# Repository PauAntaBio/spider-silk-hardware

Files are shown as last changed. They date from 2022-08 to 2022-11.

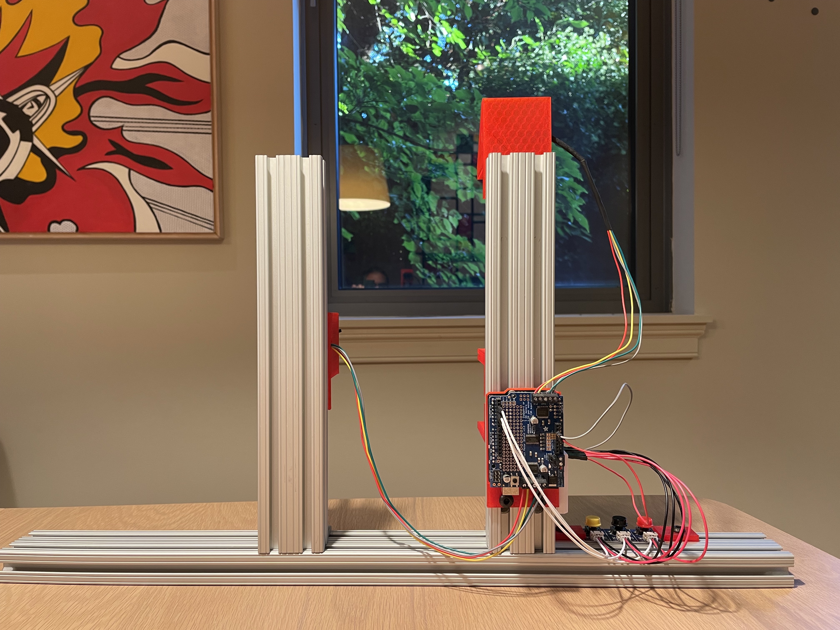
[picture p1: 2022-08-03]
pictures/3 back.jpg

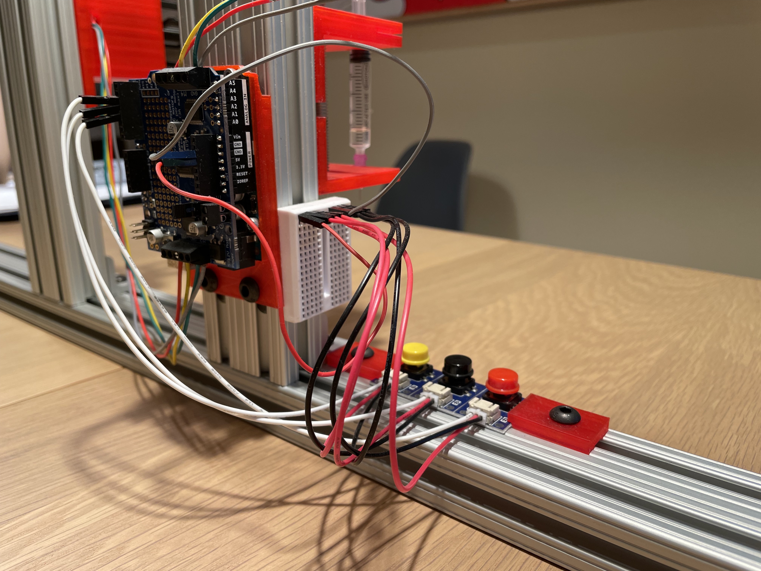
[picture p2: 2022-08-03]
pictures/4 details.jpg

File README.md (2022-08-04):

# spider-silk-hardware

There are many techniques to spin spider silk, the easiest of which is wet spinning, in which the spidroins are dissolved in a chemical solution (for example, saturated ammonium, hexafluoroisopropanol in methanol, hexafluoroacetone hydrate in methanol, and formic acid in methanol) before entering a coagulation bath that removes the solvent and causes conformational changes [1, 2]. To do wet spinning, we need a microsyringe pump capable of extruding the dope at a flowrate as slow as 1 μL/min into a coagulation bath. Once the spidroins have coagulated, a post-spinning roller will collect the spider silk. Because of the microsyringe pump’s design, shear force will help in the coagulation process of the spidroins [1, 2, 3]. Moreover, once the spidroins and gold nanoparticles are in the syringe the oxygen will be purged with Nitrogen gas to increase the chances of binding the gold nanoparticles and spidroins together.



Figure. A) Microsyringe Pump based on a micro-controller-enabled stepper motor that pushes the syringe at the desired flowrate; B) Coagulation bath where the spidroins will be pushed into. This will be filled with a chemical such as isopropanol; and C) Post-spinning roller that will collect spider silk after it has coagulated.

References

1. Rising, A., Johansson, J. Toward spinning artificial spider silk. Nat Chem Biol 11, 309–315 (2015). https://doi.org/10.1038/nchembio.1789.
2. Madurga, R., Gañán-Calvo, A. M., Plaza, G. R., Guinea, G. V., Elices, M., & Pérez-Rigueiro, J. (2017). Production of High-Performance Bioinspired Silk Fibers by Straining Flow Spinning. Biomacromolecules, 18(4), 1127-1133. https://doi.org/10.1021/acs.biomac.6b01757.
3. Andersson, M., Jia, Q., Abella, A., Lee, X.-Y., Landreh, M., Purhonen, P., Hebert, H., Tenje, M., Robinson, C. V., Meng, Q., Plaza, G. R., Johansson, J., & Rising, A. (2017). Biomimetic spinning of artificial spider silk from a chimeric minispidroin. Nature Chemical Biology, 13(3), 262-264. https://doi.org/10.1038/nchembio.2269.

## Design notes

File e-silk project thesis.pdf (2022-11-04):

# E-Silk: Electrically Conductive Spider Silk

Pau Anta-Clusella, pauanta@icloud.com
https://www.pauanta.bio/e-silk
https://github.com/PauAntaBio/spider-silk-hardware Washington DC.
Draft: August 2022

## Introduction

Spider silk is a biomaterial with excellent physical properties such as high tensile strength, high stretchiness, and high toughness [1, 5, 7]. Because of the fierce nature of spiders, the current method of spider silk production involves producing recombinant spidroins in bacterial systems and spinning them into silk [2, 3, 8]. However, the use of denaturation during the purification and fiber formation of the spidroins leads to spider silk with dissatisfying mechanical properties [5].

Presented within is a novel application for synthetic spider silk: spider silk with electrical conductivity, which could be used in clothing to create circuits or expand the current applications of smart fabrics. Some examples include: stretch sensors, functional buttons, and circuitry that can activate a small device.

By taking advantage of genetic engineering techniques a recombinant spider silk protein was created and expressed in E. coli. This spidroin consists of a N-terminus from major ampullate (MaSP) silk with a repetitive region and C-terminus from minor ampullate silk (MiSP). Further, by adding a tetracysteine motif the spidroin should gain the ability to bind to gold (Au) nanoparticles via disulfide bonds [4]. Gold was chosen for its resistance to oxidation and electrical conductivity.

## Design of Custom Protein

Spidroins vary in length and size but generally consist of three parts: a non-repetitive globular N terminus (NT), an extensive glycine- and alanine-rich repetitive region, and a nonrepetitive globular C terminus (CT) [3]. The NT subunits are bundles of 5 alpha helices; at pH levels above 7 they are monomeric, but dimerizes at pH levels below 6. The dimerization process consists of the alpha helices shifting to form a flat dimer interface, allowing the antiparallel subunits to combine [5]. The CT is a stable and soluble homodimer at pH levels greater than 6.5, but as the pH decreases to below 5.5 it destabilizes and loses its helical structure, instead forming β-sheet fibrils. Increased pCO2 (partial pressure of CO2) also aids in unfolding by interacting with partially hidden residues in the CT [5]. The CT’s transition into β-sheet fibrils produces nuclei that may induce the transformation of the repetitive region into β-sheet polymers [5].

The custom protein was largely based off of the synthetic spider silk developed by the 2019 Great Bay iGem team [3]. The NT domain of the custom spidroin is from the Euprosthenops Australis MaSp (Figure 1) due to its high solubility and pH sensitivity [3, 8] while the repetitive region and CT domain is from Araneus ventricosus MiSp. Since the repetitive region is very alanine and glycine rich, so much so that the epithelial cells of spider glands have abnormally large tRNA pools for the two amino acids [5], the spidroin only contained 2 repetitive regions. Otherwise, the E. coli may not have been able to express a high amount of the proteins. A GNS linker connected the various regions together while a 6His tag was used for Ni-NTA purification. A tetracysteine (TC) motif was added to the repetitive region to allow the spidroin to bind to Au nanoparticles.

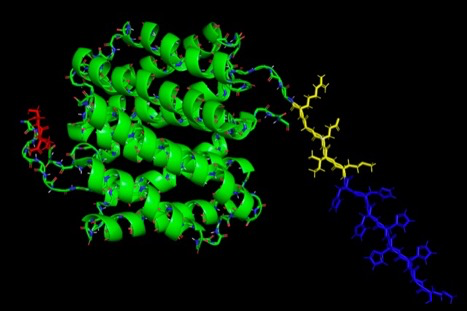
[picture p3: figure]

Figure 1. Image of the N-terminus domain of the recombinant spidroin. In red is the GNS linker, in green is the homodimer NTD, in yellow is a protease cleavage site for Factor Xa (was never implemented), and in purple is the 6His Tag.

The TC motif is an encodable motif originally designed for the in vivo imaging of proteins. It consists of 2 cysteines followed by 2 non-cysteine residues followed by 2 more cysteines (Cys - Cys - X1 - X2 - Cys - Cys) [4, 6]. The thiols of the cysteines are intended to bind to biarsenical dyes which then fluoresce, but the TC motif could also be capable of binding to the surface molecules on Au nanoparticles via disulfide bonds. Moreover, by making the 2 middle amino acids proline and glycine, respectively, the TC motif forms a beta-hairpin structure that controls the orientation of the Au nanoparticles [4, 6].

## DNA Sequence and Expression

The following sequence (Figure 2) encodes for the aforementioned spidroin with a NT domain from Euprosthenops Australis MaSp, a repetitive region and CT domain is from Araneus ventricosus MiSp, a TC Motif, a 6His Tag, and GNS linkers. The DNA plasmid was ordered from Atum (www.atum.bio) in an E.coli expression vector with an IPTG-inducible T5 promoter and a resistance to chloramphenicol.

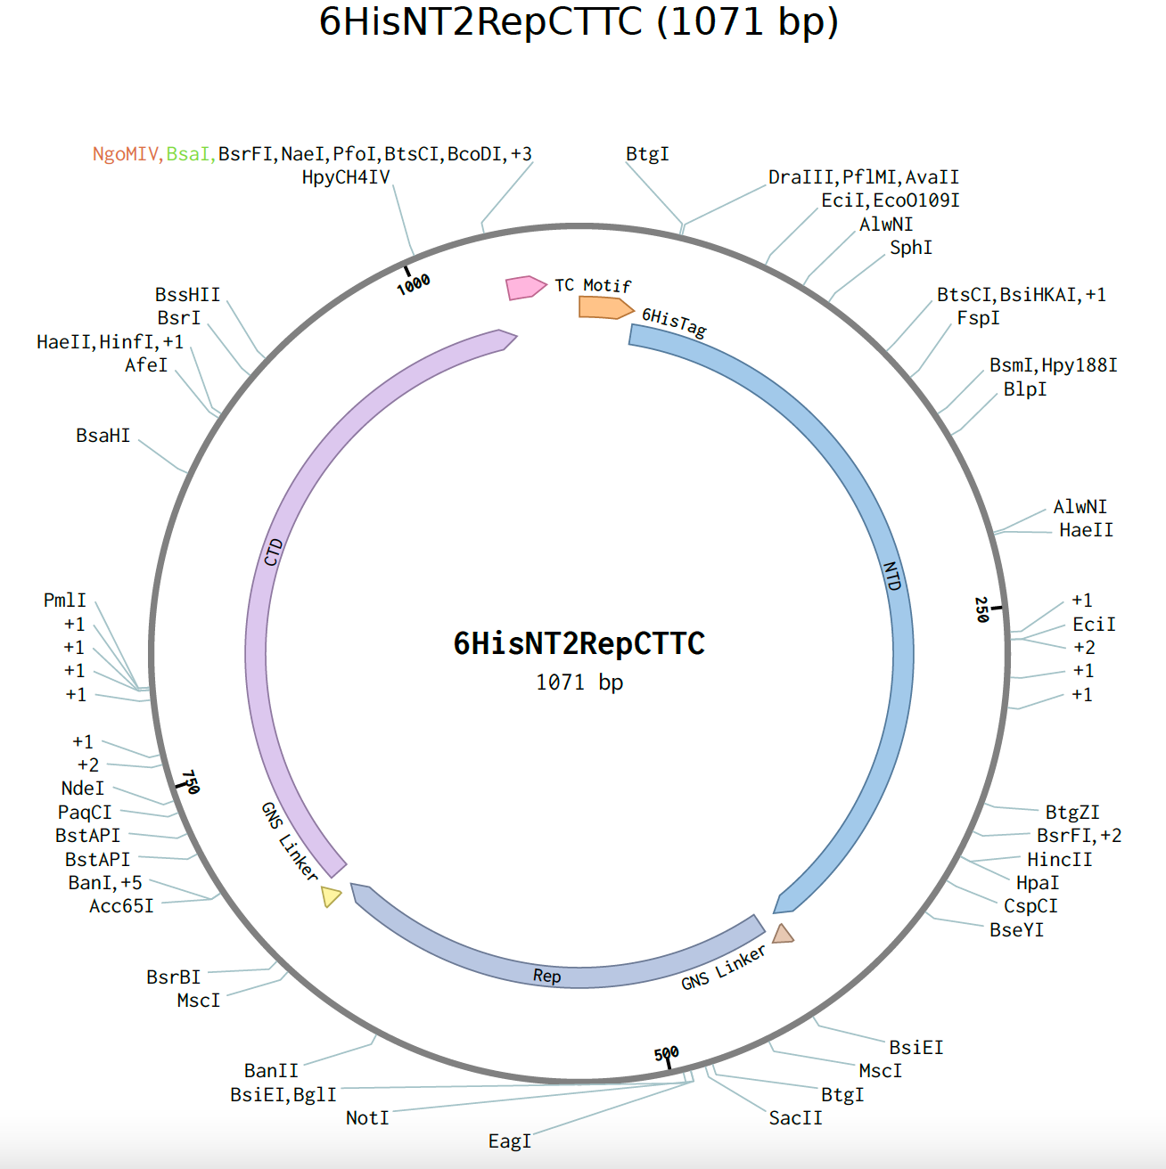
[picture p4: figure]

Figure 2. DNA sequence of the custom spider silk protein

Due to the cost of synthesizing DNA, it was not possible to order two separate plasmids, one with and the other without the TC Motif, to compare the properties of normal synthetic spider silk and electrically conductive spider silk. Instead, a NgoMIV and BsaI cut site (highlighted in orange and green, respectively), were introduced on both sides of the TC motif to remove it via a double digest.

## Nanoparticles

The reasoning for using Au nanoparticles is that gold resists oxidation and conducts electricity very well, and by binding it to spidroins, they should in theory gain electrical conductivity. A 120 ml sample of 100 ppm Au nanoparticle dispersion in water was ordered from US Research Nanomaterials, Inc (https://www.us-nano.com). The Au nanoparticles were produced using 99.99% pure gold as raw materials and were 14 nm in diameter. They were stored at room temperature in dark conditions and were sonicated before each use in order to undo any aggregation of the nanoparticles.

## Microsyringe Pump and Capture Roller

There are many techniques to spin spider silk, the easiest of which is wet spinning, in which the spidroins are dissolved in a chemical solution before entering a coagulation bath that removes the solvent and causes conformational changes [5, 7]. There are many combinations of solvents and coagulation baths, such as concentrated aqueous solution in saturated ammonium, hexafluoroisopropanol in methanol, hexafluoroacetone hydrate in methanol, and formic acid in methanol [7].

To perform wet spinning, a microsyringe pump was created from scratch based off of an open-source design found on GitHub [10]. While keeping the same bill of materials, the microsyringe pump was adapted to extrude the spidroins vertically (Figure 3A) into an acrylic case which contained the coagulation bath (Figure 3B). A post-spinning capture roller (Figure 3C) was added to collect the spider silk as it was coagulated. The coding was done entirely from scratch in Arduino IDE with the intention of being able to extrude the dope at speeds as slow as 1 µL/min. Some parts were custom designed and 3D

A

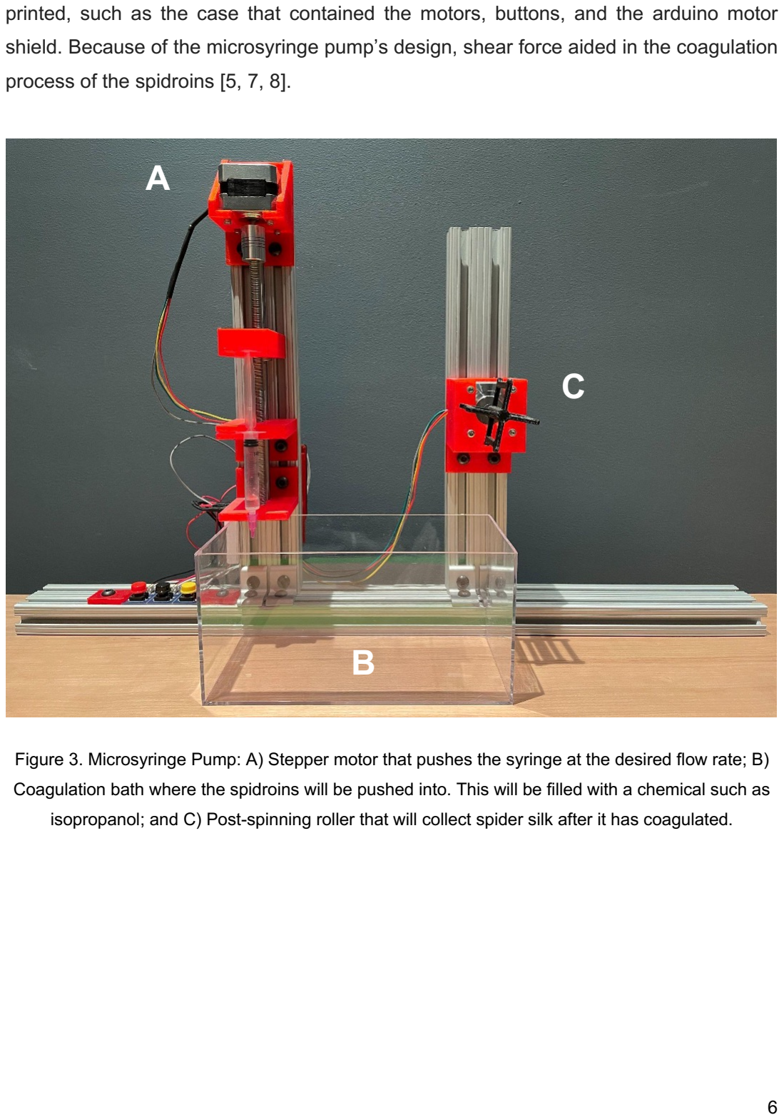
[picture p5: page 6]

printed, such as the case that contained the motors, buttons, and the arduino motor shield. Because of the microsyringe pump’s design, shear force aided in the coagulation process of the spidroins [5, 7, 8].

Figure 3. Microsyringe Pump: A) Stepper motor that pushes the syringe at the desired flow rate; B) Coagulation bath where the spidroins will be pushed into. This will be filled with a chemical such as isopropanol; and C) Post-spinning roller that will collect spider silk after it has coagulated.

C

B

## Experiment

The DNA plasmid arrived in a filter paper and was extracted by incubating it at room temperature with water for 2 minutes and centrifuging it at maximum speed for 10 minutes. As the water flowed through the filter paper it collected the DNA at the bottom of the centrifuge tube. The filter paper was discarded and part of the DNA was used to transform E.coli cells in a solid culture. The cells grew overnight and were used in a miniprep to amplify the amount of DNA plasmids available for experimentation. The concentration of amplified plasmids was determined via a spectrophotometer and then used in a DNA double digest and ligation with NgoMIV and BsaI to create a sample of DNA without the TC motif.

If the DNA had been ligated properly, the NgoMIV cut site should have been removed while the BsaI cut site was maintained. To test whether the TC motif was properly removed, separate DNA digests were done with the ligated DNA and BsaI and NgoMIV. The samples were then separated by gel electrophoresis (Figure 4). Since DNA plasmids travel slower when they have been digested, the expected results for a successful removal of the TC motif would have been band 4A traveling the furthest, band 4B traveling a similar distance, and band 4C and 4D traveling a noticeably shorter distance than the others. Instead, band 4A was observed to travel the furthest while bands 4B, 4C, and 4D traveled approximately the same distance (Figure 4). From this it can be concluded that the TC motif was not properly removed from the DNA plasmids. Due to time constraints I was unable to repeat the digest and try to obtain plasmids without the TC motif.

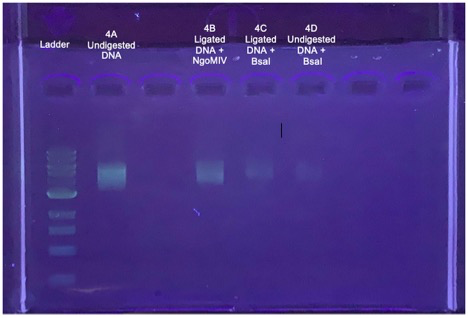
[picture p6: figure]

Figure 4. Gel electrophoresis of ligated and undigested DNA with NgoMIV and BsaI. From left to right, the samples are a ladder and 20 µl of the original, undigested DNA with the TC motif, the ligated DNA from the double digest with NgoMIV, the ligated DNA from the double digest with BsaI, and the original, undigested DNA with BsaI.

E.coli cells were transformed with the amplified DNA plasmids and grown in a solid culture overnight. They were then induced with IPTG and allowed another day to produce the spidroins, after which they were collected and lysed. Part of the whole-cell lysate was reserved while the other part was purified via Nickel-NTA purification. However, the results of the proteins being analyzed via mass-spectroscopy were completely unexpected and suggested that the proteins might not have been properly purified.

1ml samples of the whole-cell lysate and purified proteins were placed in 27 G and 30 G syringes with varying needle diameters and extruded at different speeds into a coagulation bath of isopropanol. Ultimately, spider silk was produced from the whole cell lysate in a 27 G syringe with a tip of 0.21 mm diameter at an extrusion speed of 15 µl/min (Figure 5). It is possible that the purified proteins were not eluded properly or diluted so much that they could not properly form strands of spider silk.

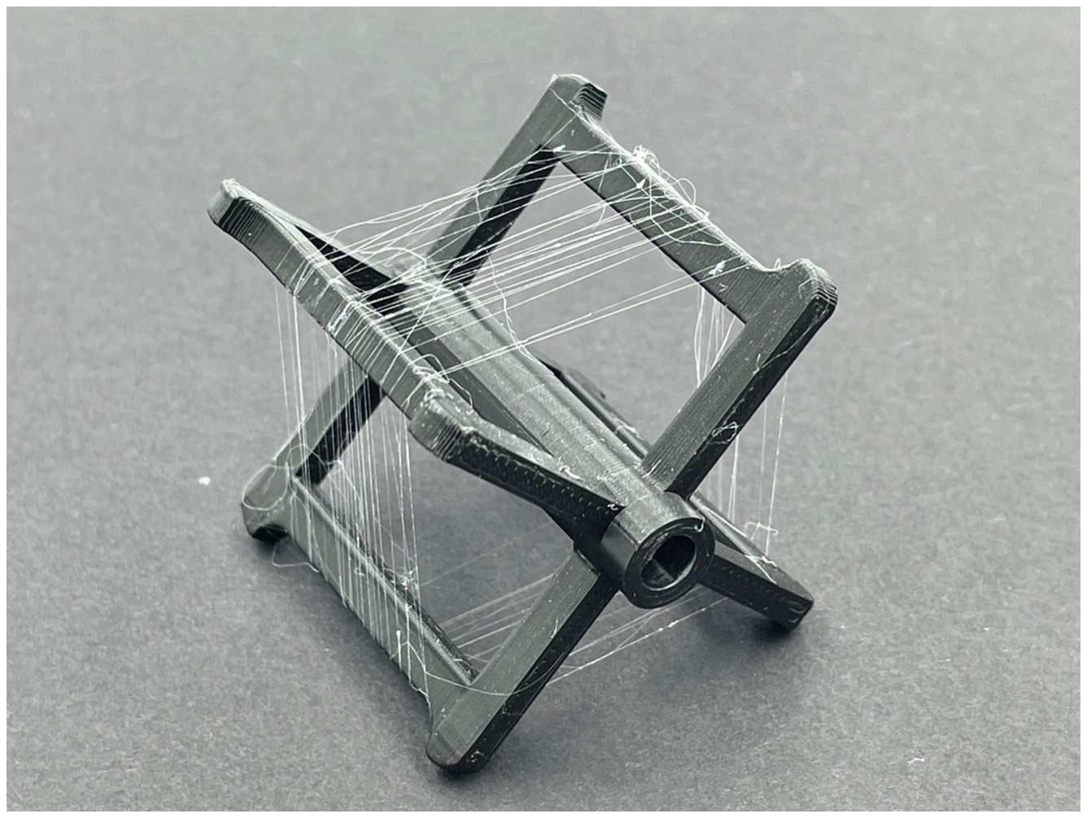
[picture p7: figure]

Figure 5. Spider silk produced from whole-cell lysate in an isopropanol coagulation bath.

Before binding the Au nanoparticles to the spider silk proteins, the Au nanoparticles were sonicated for 15 minutes to undo any aggregation. A small hole was drilled into the side of a syringe where a tube was placed connecting it to a nitrogen gas tank. Due to the success of the lysate in producing spider silk, a 3 ml sample of the lysate was mixed in the syringe with 1 ml of Au nanoparticle solution and nitrogen gas was introduced via the hole in the syringe. Nitrogen gas was added since it is chemically inert and by purging the oxygen from the syringe the Au nanoparticles should have oxidized less and been more capable of binding to the proteins. However, the protein and Au nanoparticle solution was not able to produce any strands of spider silk, and due to time constraints I was unable to pursue the issue any further.

## Moving Forward

It will be extremely important to properly purify the proteins and obtain them in a high concentration. This should overcome the initial issue of the purified proteins not producing any silk compared to the lystate. Also, more research will have to be done towards finding the optimal ratio of Au nanoparticles to proteins and whether the Au nanoparticles should be a different size. Something else to consider is whether the protein’s design should be changed to have multiple TC motifs or if the TC motif should be included at all. Other options to help the proteins bind to Au nanoparticles might be to replace certain residues with cysteines or to include long sequences with only cysteines. With these considerations and others in mind, I am optimistic about retaking this project in the future and producing synthetic spider silk that conducts electricity!

## References

1. Vienneau-Hathaway, J.M., Brassfield, E.R., Lane, A.K. et al. Duplication and concerted evolution of MiSp-encoding genes underlie the material properties of minor ampullate silks of cobweb weaving spiders. BMC Evol Biol 17, 78 (2017). https://doi.org/10.1186/s12862-017-0927-x.
2. Deptuch, T., & Dams-Kozlowska, H. (2017). Silk Materials Functionalized via Genetic Engineering for Biomedical Applications. Materials, 10(12), 1417. https://doi.org/10.3390/ma10121417.
3. Li, C., Liu, J., & Yang, J. (n.d.). Spidroin Engineering with Chromoprotein and Natural Dye. https://2019.igem.org/Team:GreatBay_SZ.
4. Reed, A. M. W. (n.d.). The Genetically Encodable Oriented Adsorption of Proteins onto Gold Nanoparticles [Doctoral dissertation]. Digital Georgetown. https://repository.library.georgetown.edu/handle/10822/557940.
5. Rising, A., Johansson, J. Toward spinning artificial spider silk. Nat Chem Biol 11, 309–315 (2015). https://doi.org/10.1038/nchembio.1789.
6. Langmuir 2010, 26, 24, 18945–18950 Publication Date:November 29, 2010 https://doi.org/10.1021/la1035135.
7. Madurga, R., Gañán-Calvo, A. M., Plaza, G. R., Guinea, G. V., Elices, M., & Pérez-Rigueiro, J. (2017). Production of High Performance Bioinspired Silk

Fibers by Straining Flow Spinning. Biomacromolecules, 18(4), 1127-1133. https://doi.org/10.1021/acs.biomac.6b01757.

8. Andersson, M., Jia, Q., Abella, A., Lee, X.-Y., Landreh, M., Purhonen, P., Hebert, H., Tenje, M., Robinson, C. V., Meng, Q., Plaza, G. R., Johansson, J., & Rising, A. (2017). Biomimetic spinning of artificial spider silk from a chimeric minispidroin. Nature Chemical Biology, 13(3), 262-264. https://doi.org/10.1038/nchembio.2269.
9. Love, J. C., Estroff, L. A., Kriebel, J. K., Nuzzo, R. G., & Whitesides, G. M. (2005). Self-Assembled Monolayers of Thiolates on Metals as a Form of Nanotechnology. Chemical Reviews, 105(4), 1103-1170. https://doi.org/10.1021/cr0300789
10. Theo Walker. 2014. Open Syringe Pump. https://github.com/manimino/OpenSyringePump.

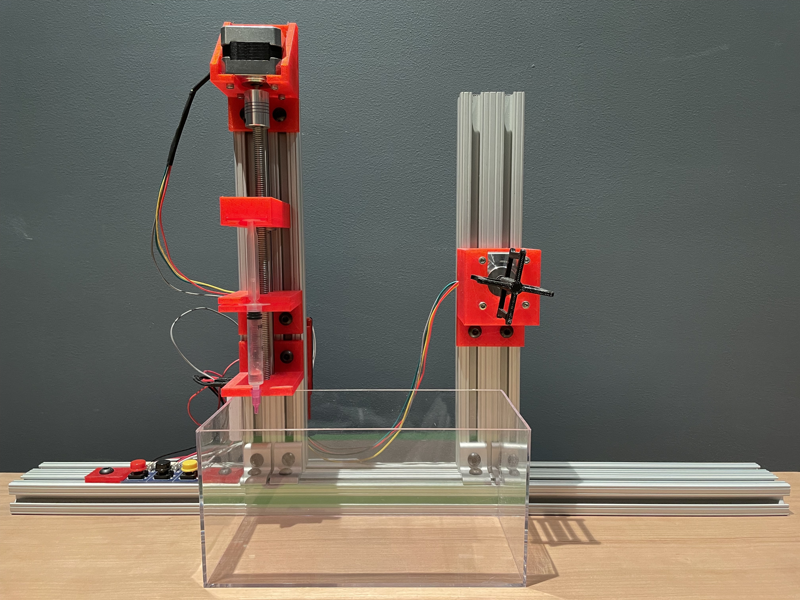
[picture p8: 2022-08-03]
pictures/1 front .jpg

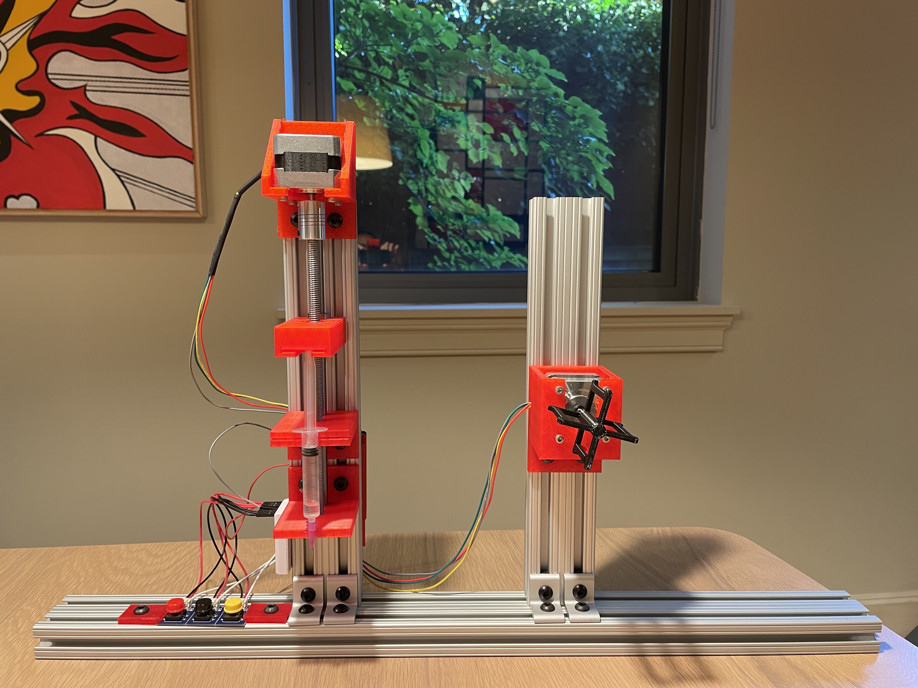
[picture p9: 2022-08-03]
pictures/2 front.jpg

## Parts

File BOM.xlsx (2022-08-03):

Bill of Materials (BOM)
Updated: August 2022
Part Name | Vendor | Part Number | Description | qty | cost | total
Hardware
316 Stainless Steel Threaded Rod (https://www.mcmaster.com/94185A160) | McMASTER-CARR | 94185A160 | M8 1m Steal Rod, 1.25mm Pitch | 1 | 19.63 | 19.63
316 Stainless Steel Hex Nut (https://www.mcmaster.com/94150A355) | McMASTER-CARR | 94150A355 | 50 Pack - M8 1.25mm Thread Hex Nut (Pack 50) | 1 | 21.76 | 21.76
Carbon Steel Linear Motion Shaft (https://www.mcmaster.com/6112K45) | McMASTER-CARR | 6112K44 | 8mm Diameter, 200mm Long | 1 | 7.21 | 7.21
Fixed Alignment Linear Ball Bearing (https://www.mcmaster.com/61205K75) | McMASTER-CARR | 61205K75 | for 8mm Shaft Diameter | 1 | 20.69 | 20.69
1x2x18" Aluminum Extrusion (https://www.mcmaster.com/47065T107/) | McMASTER-CARR | 47065T107 | T-slotted Extrusion - length 2" | 1 | 18.39 | 18.39
1x2x18" Aluminum Extrusion (https://www.mcmaster.com/47065T107/) | McMASTER-CARR | 47065T107 | T-slotted Extrusion - length 1" | 2 | 12.68 | 25.36
Silver corner bracket | McMASTER-CARR | 47065T236 | Silver Corner Bracket, 1" Long for 1" High Rail T-Slotted Framing | 4 | 7.92 | 31.68
Socket Cap Screw and T-Nut (https://www.amazon.com/dp/B00FDSEOWY?linkId=bb4feeb4c1c7025011836c82b5f66812&language=en_US) | Amazon | N/A | 1/4-20 x .5" Button Head Socket Cap Screw (BHSCS) and Slide-in T-Nut (Pack 25) | 1 | 17.99 | 17.99
5x8mm Motor Shaft Coupler (https://www.amazon.com/dp/B00KHTVOEU?linkId=8e3a22bfafcd123dfacb3b5443177c7b&language=en_US) | Amazon | N/A | 5mm x 8mm Motor Shaft Helical Beam Coupler Coupling 18mm Dia 25mm Length | 1 | 5.99 | 5.99
Stainless Steel Screws and Nuts (https://www.amazon.com/gp/product/B071KBVZVV/ref=ppx_yo_dt_b_asin_title_o06_s00?ie=UTF8&psc=1) | Amazon | N/A | VIGRUE M2-M3-M4-1080PCS Stainless Steel Screws and Nuts, 1080 Pcs Hex Socket Head Cap | 1 | 25.99 | 25.99
Electronics
Arduino Uno Rev3 (https://store-usa.arduino.cc/products/arduino-uno-rev3?selectedStore=us) | Arduino | A000066 | Microcontroller board based on the ATmega328P | 1 | 27.60 | 27.60
Motor Shield (https://www.adafruit.com/product/1438) | Adafruit | 1438 | Adafruit Motor/Stepper/Servo Shield for Arduino v2 Kit - v2.3 | 1 | 19.95 | 19.95
Stepper Motor NEMA17 (https://www.adafruit.com/product/324) | Adafruit | 324 | Stepper motor - NEMA-17 size - 200 steps/rev, 12V 350mA | 2 | 14.00 | 28.00
Breadboard (https://www.adafruit.com/product/65) | Adafruit | 65 | Tiny breadboard | 1 | 4.00 | 4.00
Buttons (https://www.adafruit.com/product/4431) | Adafruit | 4431 | STEMMA Wired Tactile Push-Button Pack (Pack 5) | 1 | 7.50 | 7.50
 |  |  |  |  |  | 281.74
Tools
Allen keys set
Digital multimeter
Wire strippers
Jumper wires

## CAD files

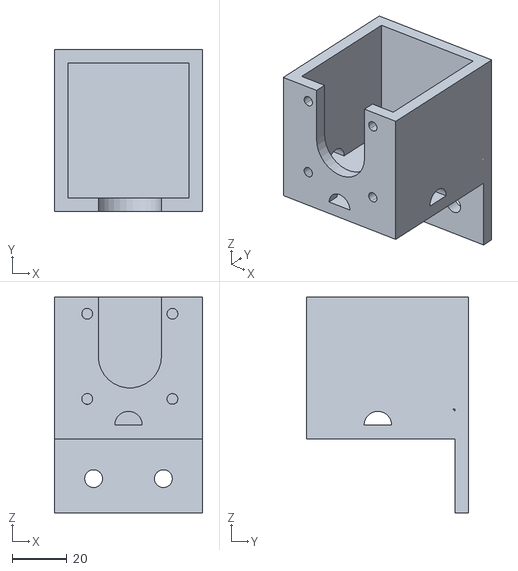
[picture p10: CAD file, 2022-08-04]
3D parts/motorHMount.stl
54.0 x 59.0 x 78.6

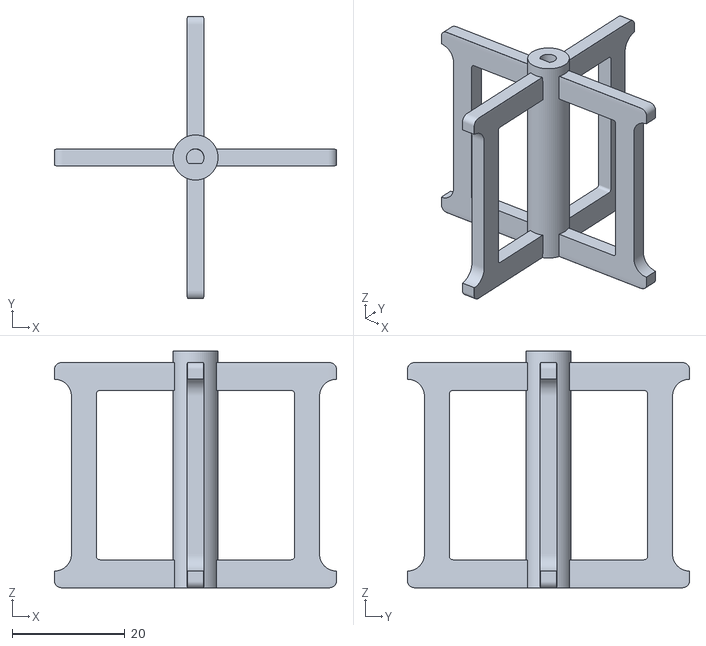
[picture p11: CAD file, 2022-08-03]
3D parts/captureRoll.stl
50.0 x 50.0 x 42.0

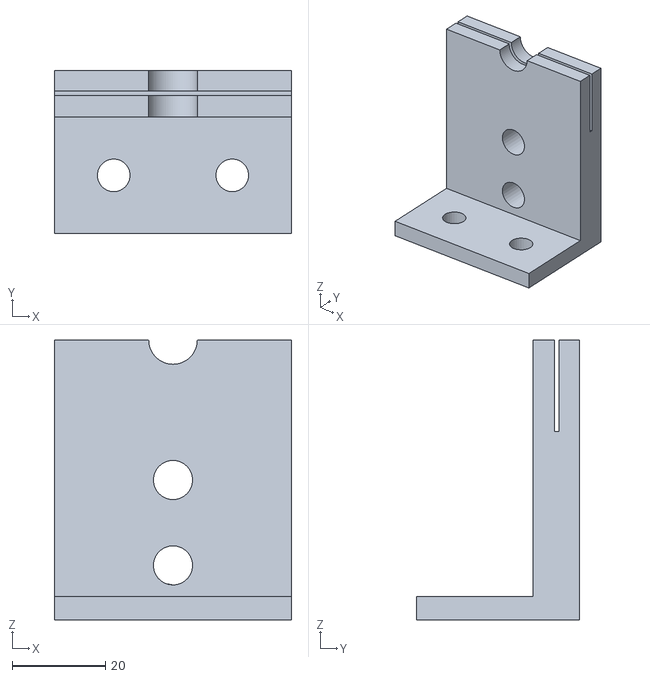
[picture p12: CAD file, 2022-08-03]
3D parts/rodMountBarrel.stl
50.8 x 35.0 x 60.0

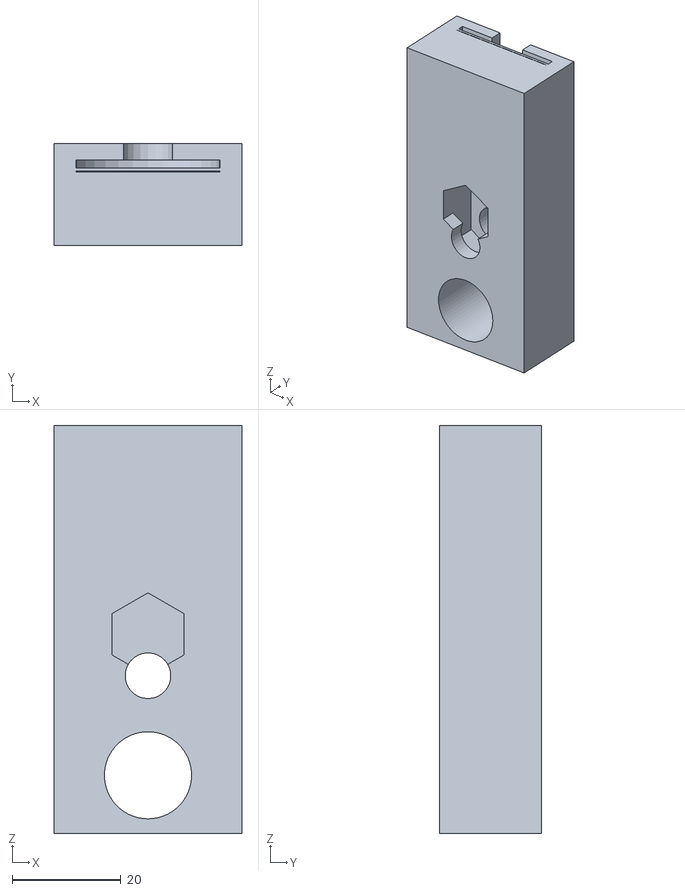
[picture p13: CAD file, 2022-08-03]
3D parts/rodMountPlunger.stl
34.5 x 18.7 x 75.0

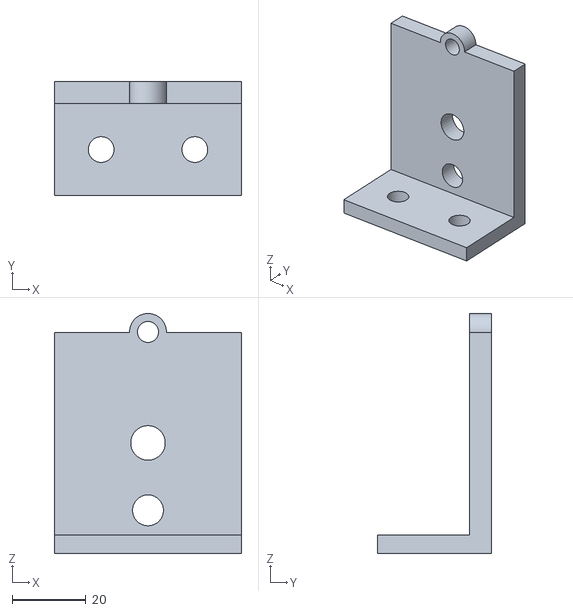
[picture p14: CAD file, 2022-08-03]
3D parts/rodMountSyringe.stl
50.8 x 31.0 x 65.1

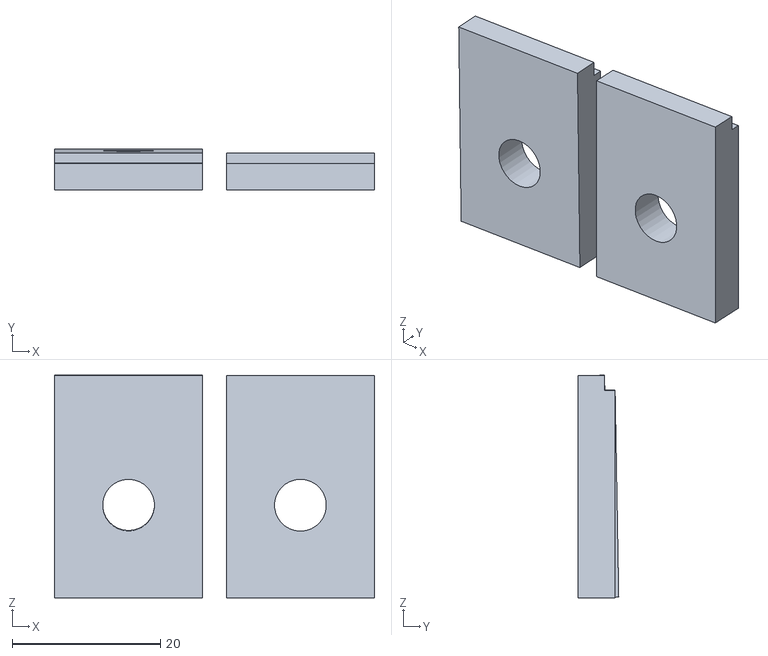
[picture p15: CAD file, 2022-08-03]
3D parts/buttonHolders.stl
43.2 x 5.47 x 30.1

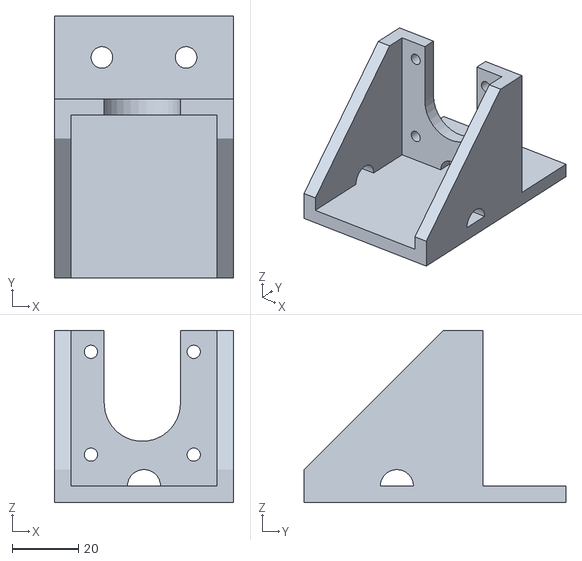
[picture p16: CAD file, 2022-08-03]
3D parts/motorVMount.stl
54.0 x 79.0 x 52.0

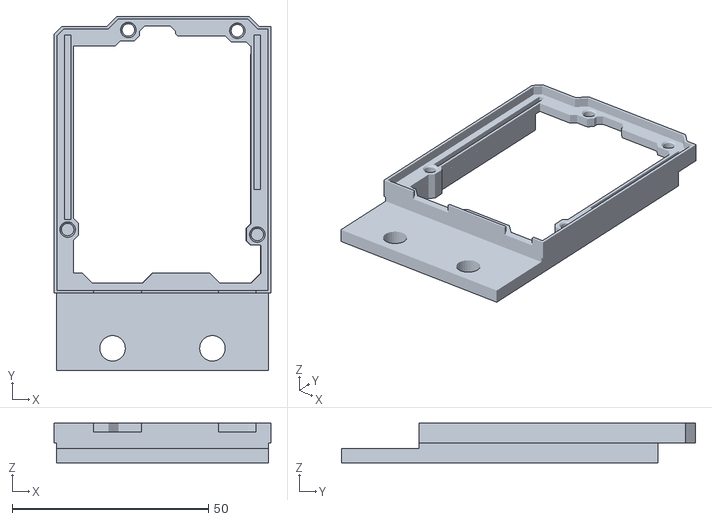
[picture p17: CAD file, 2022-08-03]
3D parts/arduinoUnoMount.stl
55.2 x 90.2 x 10.1

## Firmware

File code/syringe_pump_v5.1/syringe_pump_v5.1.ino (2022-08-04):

// Project e-Silk: synthetic spider silk with electrical conductivity
// by Pau Anta, more info at https://www.pauanta.bio.

// Development of a programmable device consisting of a micro-syringe pump and a spinning machine, based on Arduino microcontroller.
// The micro-syringe pump pushes the spidroins dope into a coagulation bath, at a programmable flowrate,
// and the spinning machine will spin the silk threads into a capture roller, also at the desired speed.

// Hardware inspired by the OpenSyringePump developed by Naroom, https://github.com/manimino/OpenSyringePump. All software is original.
// Started project on March 2020.

// ALERT: The maximum flowrate of this microsyringe pump is 12.4 µL/min with the current specifications (changes with motor speed, thread size, and syringe needle radius)

#include <Wire.h>
#include <Adafruit_MotorShield.h>
#include "utility/Adafruit_MS_PWMServoDriver.h"
#include <math.h>
#define PI

Adafruit_MotorShield AFMS = Adafruit_MotorShield(); 
Adafruit_StepperMotor *myMotorV = AFMS.getStepper(200, 2);      // Stepper motor for the microsyringe pump, facing down
Adafruit_StepperMotor *myMotorH = AFMS.getStepper(200, 1);      // Stepper motor for the capture roller, facing sideways

const int UpButton = 2;                   // Button to move plunge up manually
const int DownButton = 3;                 // Button to move plunge down manually
const int StartStopButton = 4;            // Button to start/stop movement of microsyringe at predetermined flowrate

int DownButtonState = 0;
int UpButtonState = 0;
int StartStopButtonState = 0;

const float SyringeRadius = 4.4;          // Inner radius of the syringe in mm. NEED TO SET UP BASED ON YOUR SYRINGE
float FlowRate = 3;                       // How fast the dope is pushed out of the syringe in µL/min. NEED TO SET UP AT YOUR DESIRED FLOW RATE
float DopeVolume = 0.5;                   // The volume of spidroin dissolved in a chemical in mL
float CaptureSpeed = 0.2;                 // The speed of the capture motor in meters per minute. NEED TO SET UP AT A DESIRED CAPTURE SPEED
float MaxFlowRate;                        // The maximum flow rate, depends on the thread size and the radius of the syringe

const float ThreadSize = 1.25;            // Thread size of the threaded rod in mm
const float TimePerStep = 3.8;            // Time it takes the motor to make 1 step in ms.

const int StepsPerRevolution = 200;       // 200 steps equal a single 360º turn of the stepper motor
const int Rebound = 2000;                 // Need this variable to control the buttons. Average time spent holding down the buttons in ms

float VolumePerStep;                      // The dope volume pushed per 1 step, in µL
float VolumePerRevolution;                // The dope volume pushed per 200 steps, in µL
float FlowRateInSteps;                    // The flowrate in steps
float VTotalSteps;                        // Number of steps to push out all the dope
int StepCounter = 0;
float DopeRemaining;                      // The volume of dope remaining
float DopeProgress;                       // Percentage of dope pumped    
float VTimeForAllSteps;                   // The time it takes to do all microsteps not including the delay in between for the syringe (vertical) motor
float VMotorInterval;

float Progress = 0;
float TimeRemaining;

float HMotorThreshold = 2.5;              // The percentage of dope that must be ejected for the capture motor to begin working

const float DistancePerRevolution = 0.1335;  // The length of spider silk captured per revolution in meters
float DistancePerStep;                    // The length of spider silk captured per step in meters                       
float HTimeForAllSteps;                   // The time it takes to do all microsteps not including the delay inbetween for the capture (horizontal) motor
float CaptureSpeedInSteps;
float HMotorInterval;                  

unsigned long VPreviousMotorTime;
unsigned long HPreviousMotorTime;

unsigned long VCurrentMotorTime;
unsigned long HCurrentMotorTime;

float TimeNow;
float TimeElapsed;


void setup() {
  
  Serial.begin(57600);

  AFMS.begin();
  
  pinMode(DownButton, INPUT);
  pinMode(UpButton, INPUT);
  pinMode(StartStopButton, INPUT);

  Serial.println("Dope volume:  " + String(DopeVolume, 5) + " mL");
  Serial.println("Flow rate in µL:  " + String(FlowRate) + " µL/min");

  unsigned long VPreviousMotorTime = millis();
  unsigned long HPreviousMotorTime = millis();

  //Calculation of total number of steps for pumping the dope volume

  VolumePerRevolution = (M_PI * ThreadSize * sq(SyringeRadius));          //Volume of dope pushed out every revolution, in cubic mm (µL)
  Serial.println("VolumePerRevolution: " + String(VolumePerRevolution, 10) + " µL/rev");
  VolumePerStep = VolumePerRevolution / StepsPerRevolution;               //Volume of dope pushed out every step, in µL / step
  Serial.println("VolumePerStep: " + String(VolumePerStep, 10) + " µL/step");
  VTotalSteps = (DopeVolume * 1000) / VolumePerStep;                      //Total number of steps to push out the entire volume
  Serial.println("VTotalSteps: " + String(VTotalSteps) + " Steps");

  //Calculation for max flowrate
  
  MaxFlowRate = (60000/TimePerStep) * VolumePerStep;                      //The maximum flow rate in µL / min
  Serial.println("Maximum flow rate " + String(MaxFlowRate, 5) + " µL/min");

  //Calculation of flowrate in steps per minute

  FlowRateInSteps = FlowRate / VolumePerStep;                             //Converts flowrate from µL/min to steps/min
  Serial.println("Flow rate in steps:  " + String(FlowRateInSteps) + " steps/min");
  
  VTimeForAllSteps = FlowRateInSteps * TimePerStep;                       //Time to complete all the steps (in ms) in one minute
  Serial.println("VMTimeForAllSteps:  " + String(VTimeForAllSteps, 10) + " miliseconds");
  VMotorInterval = (60000 - VTimeForAllSteps) / FlowRateInSteps;          //The interval between each step in ms           
  Serial.println("VMotorInterval:  " + String(VMotorInterval, 3) + " miliseconds");        
  Serial.println("Total time:  " + String(((DopeVolume * 1000) / FlowRate) / 60) + " hours");

  //Calculation for the interval of time between each step for the capture motor

  DistancePerStep = DistancePerRevolution / StepsPerRevolution;           //The length of spider silk captured by the capture roller per step
  Serial.println("DistancePerStep: " + String(DistancePerStep, 10) + " m/step");
  CaptureSpeedInSteps = CaptureSpeed / DistancePerStep;                   //Converts the capture speed from m/min to steps/min
  Serial.println("CaptureSpeedInSteps: " + String(CaptureSpeedInSteps) + " steps/min");
  HTimeForAllSteps = CaptureSpeedInSteps * TimePerStep;                   //Time to complete all steps (in ms) in one minute
  HMotorInterval = (60000 - HTimeForAllSteps) / CaptureSpeedInSteps;      //The interval between each step in ms
  Serial.println("HMotorInterval: " + String(HMotorInterval, 10) + " steps/min");

}

void loop() {
  
  DownButtonState = digitalRead(DownButton);
  if (DownButtonState == LOW) {                 
    myMotorV->step(1, FORWARD, DOUBLE);          //Makes the motor go forward as long as the Down button is held down
    StepCounter = 0;                             //Up or down buttons also reset the microstep counter
  }
  
 UpButtonState = digitalRead(UpButton);
  if (UpButtonState == LOW) {               
    myMotorV->step(1, BACKWARD, DOUBLE);         //Makes the motor go backward as long as the Up button is being held down
    StepCounter = 0;                             //Up or down buttons also reset the microstep counter
  }
  
 StartStopButtonState = digitalRead(StartStopButton);
  if (StartStopButtonState == LOW) {            //Makes the motor eject the dope at the desired flow rate
    Serial.println("Start!");
    StartPump();
    CaptureStart();  
    }
 
}

void StartPump() {                              //Makes the syringe pump push at the predetermined speed
  
  TimeElapsed = millis();

  Serial.println("Pumping Starts!");
  
  StartStopButtonState = HIGH;
  
  delay(Rebound);

  TimeNow = millis();

  while ((StartStopButtonState == HIGH) and (StepCounter < VTotalSteps)) {
    
    TimeRemaining =  millis() - TimeNow;
    unsigned long VCurrentMotorTime = millis();
    unsigned long HCurrentMotorTime = millis();
    
    if(VCurrentMotorTime - VPreviousMotorTime > (VMotorInterval + TimePerStep)){
      myMotorV->onestep(FORWARD, SINGLE);
      VPreviousMotorTime = VCurrentMotorTime;
      StepCounter = StepCounter + 1;
      DopeRemaining = (DopeVolume - ((StepCounter * VolumePerStep) / 1000));
      DopeProgress = ((DopeVolume - DopeRemaining) / DopeVolume) * 100;
      Serial.println("Dope progress " + String(DopeProgress, 1) + "%");
      Serial.println("Time remaining:  " + String(((DopeVolume * 1000) / FlowRate) - (TimeRemaining / 60000)) + " minutes");

      StartStopButtonState = digitalRead(StartStopButton);

    }

    if(HCurrentMotorTime - HPreviousMotorTime > (HMotorInterval + TimePerStep) and DopeProgress > HMotorThreshold){
      myMotorH->onestep(BACKWARD, SINGLE);
      HPreviousMotorTime = HCurrentMotorTime;
    }

    StartStopButtonState = digitalRead(StartStopButton);

   }
   
    TimeElapsed = millis() - TimeElapsed;
    Serial.println("Time elapsed: " + (String(TimeElapsed / 1000)) + "seconds");
    delay(Rebound);
    Serial.println("Pumping Done!");

  }

void CaptureStart() {

  delay(Rebound);

  StartStopButtonState == HIGH;

  Serial.println("Capture Starts!");

  while (StartStopButtonState == HIGH) {

    unsigned long HCurrentMotorTime = millis();

    if((HCurrentMotorTime - HPreviousMotorTime) > (HMotorInterval + TimePerStep)){
      myMotorH->onestep(BACKWARD, SINGLE);
      HPreviousMotorTime = HCurrentMotorTime;
   
    }
  
  StartStopButtonState = digitalRead(StartStopButton);

  }

  Serial.println("Capture Done!");
  delay(Rebound);

}
